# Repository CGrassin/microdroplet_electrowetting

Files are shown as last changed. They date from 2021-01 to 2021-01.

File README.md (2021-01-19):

# µDroplet - Microfluidics platform

Microfluidics is an area of research based on the manipulation of small fluid volumes on the order of microliters or nanoliters.

µDroplet is an open-source platform with an 8&times;8 array of electrodes driven by a high voltage to expermiment with various microfluidics techniques and materials.

See article here: https://charleslabs.fr/en/project-Microfluidics+Electrowetting+platform

## Content

This repository contains:
* The PCB (including BOM and gerber files),
* The Arduino firmware
* The Processing control software
* The STL/CAD files for the 3D-printable base and frame

## License

The content of this repository is under MIT license.

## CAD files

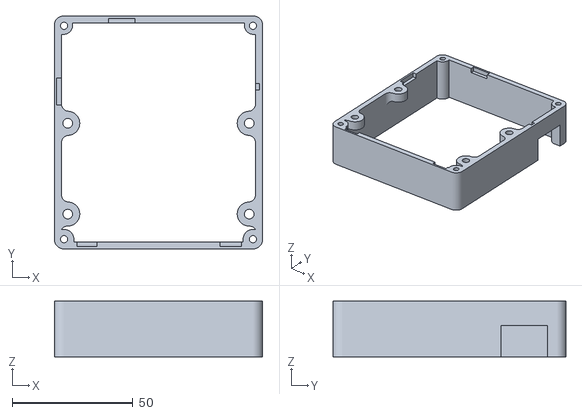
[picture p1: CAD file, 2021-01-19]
Microfluidics_CAD/microfluidics_base.STL
86.4 x 96.5 x 23.0

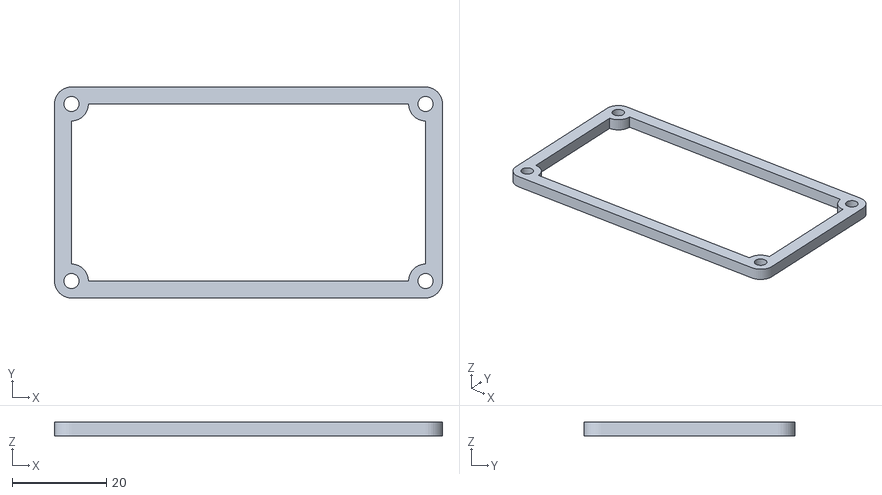
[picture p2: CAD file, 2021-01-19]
Microfluidics_CAD/microfluidics_lid.STL
82.4 x 44.8 x 3.00

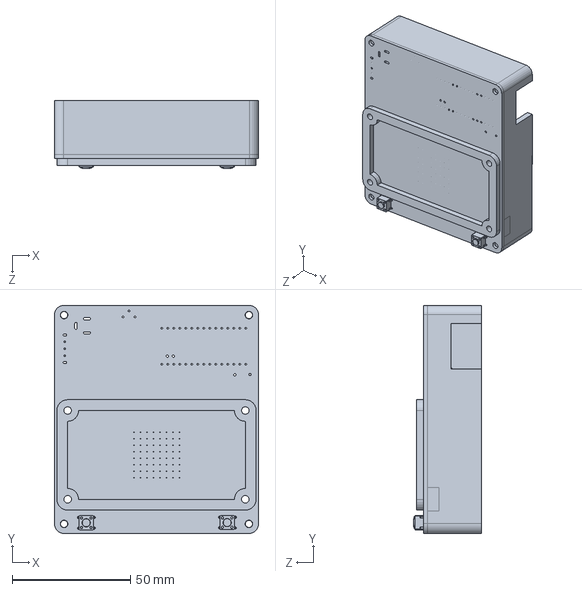
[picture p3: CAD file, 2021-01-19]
Microfluidics_CAD/MicroDroplet_PCB.SLDPRT
86.4 x 96.5 x 29.0 mm

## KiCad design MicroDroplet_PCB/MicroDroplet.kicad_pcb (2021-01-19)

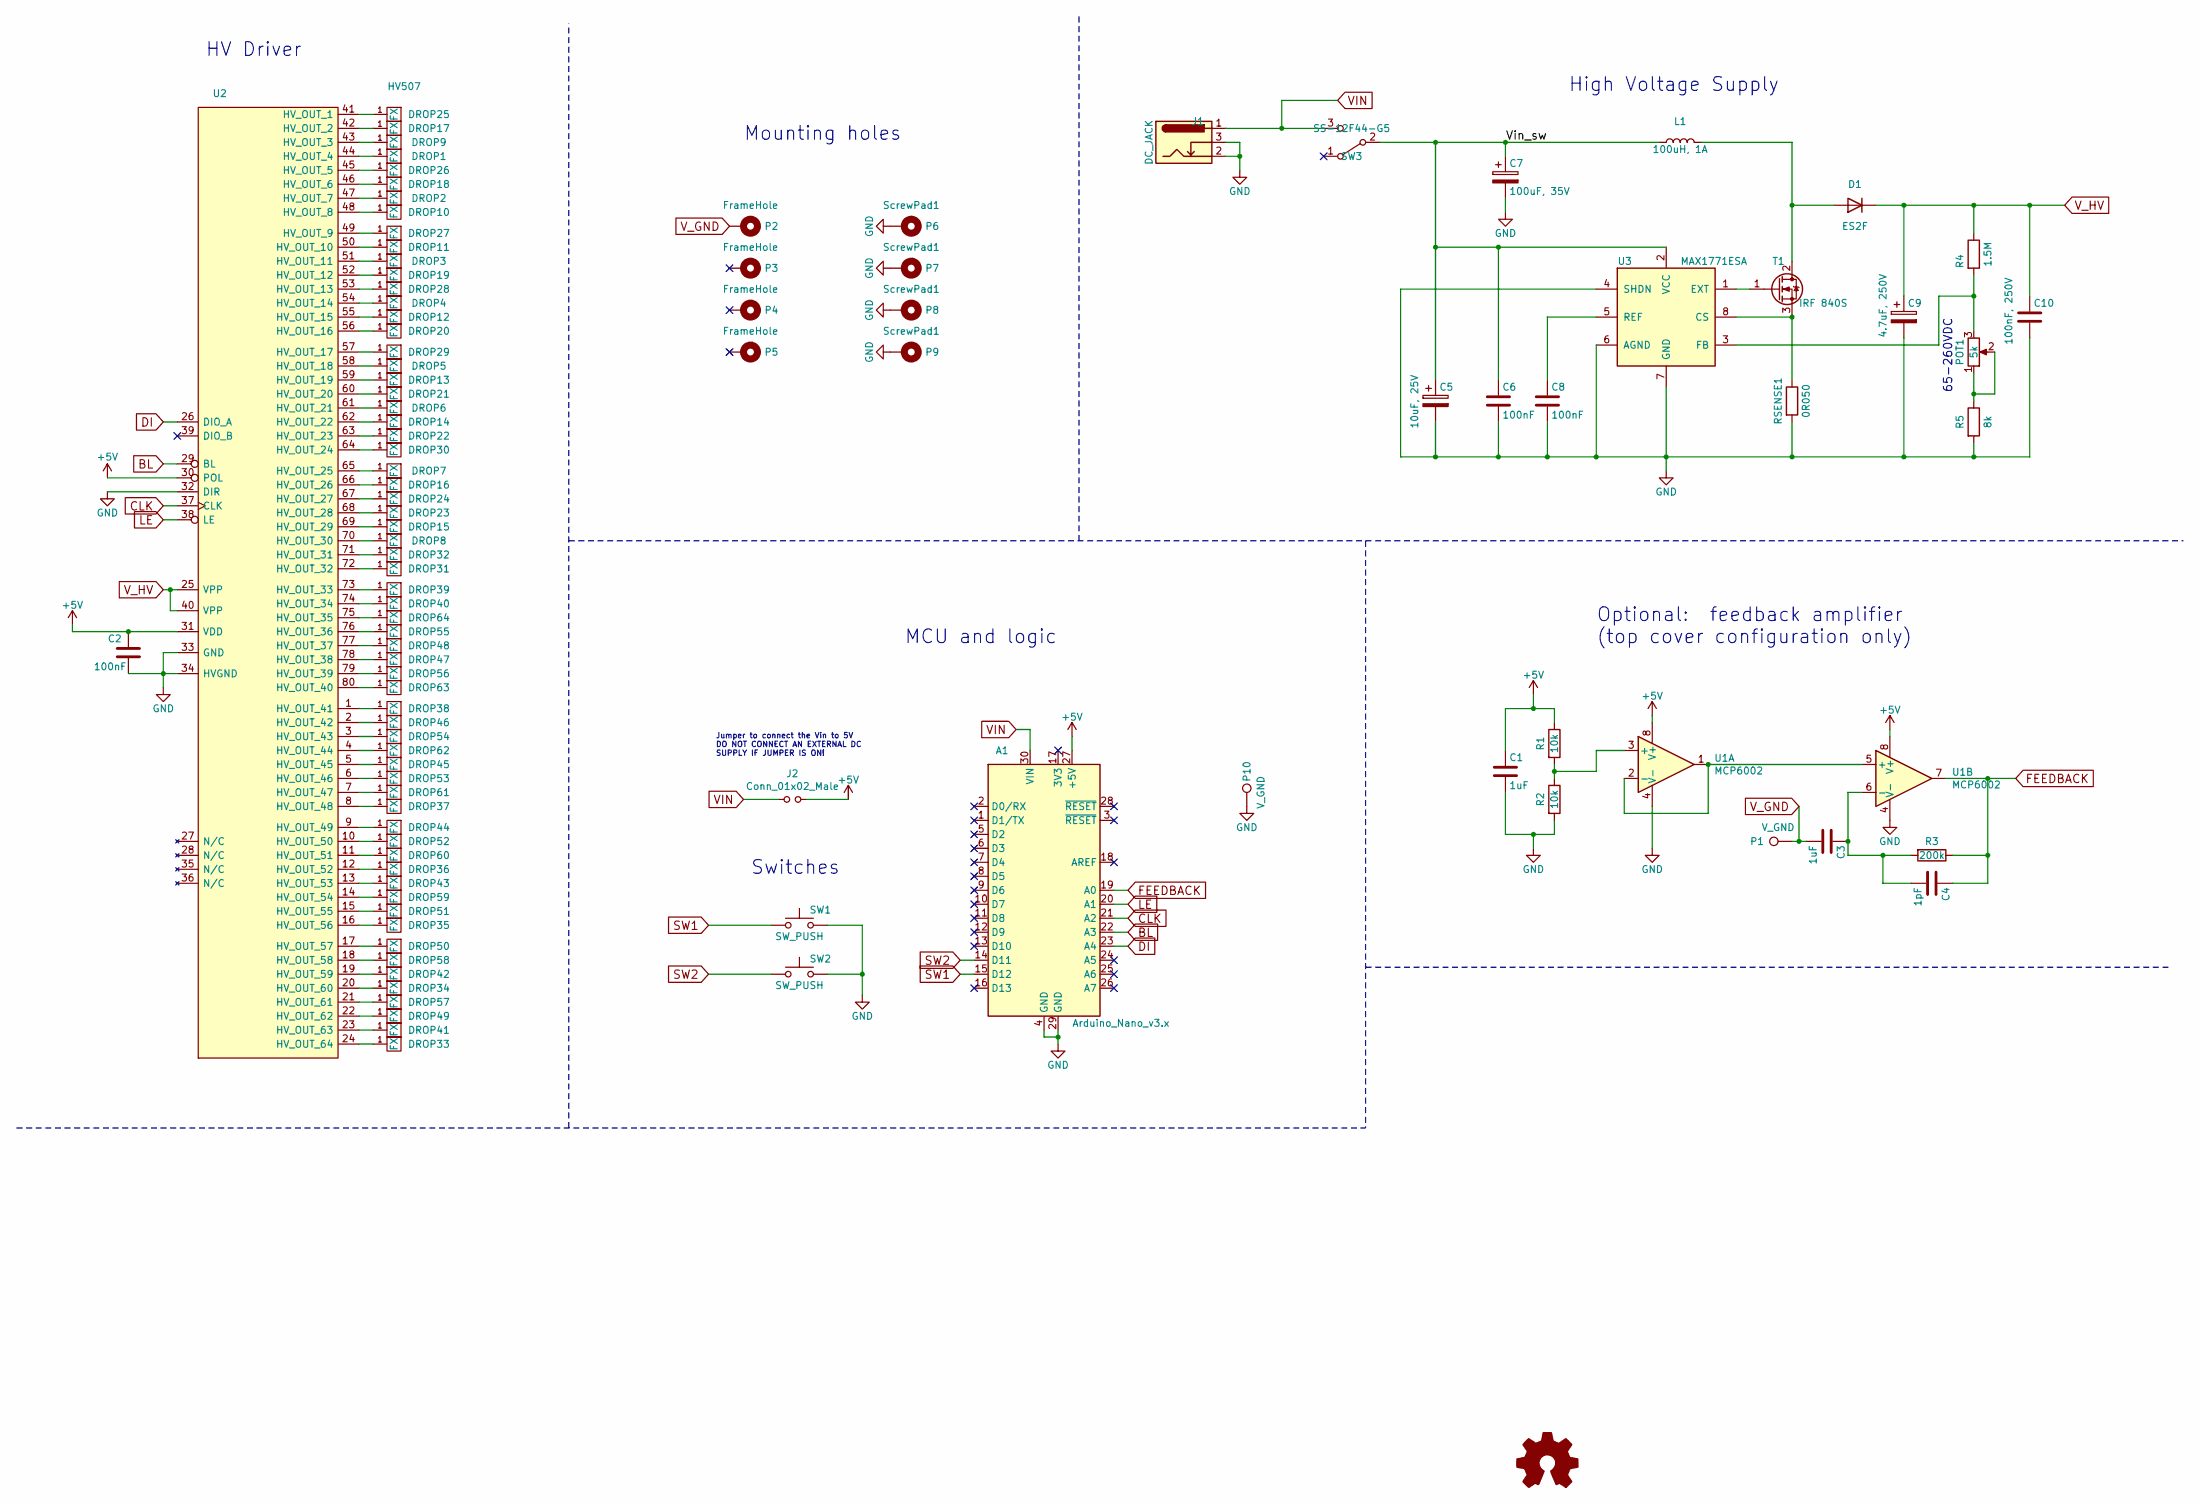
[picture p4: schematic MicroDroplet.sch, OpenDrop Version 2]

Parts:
A1: Arduino_Nano_v3.x; Arduino_Nano
C1, C3: 1uF; C_0805_2012Metric_Pad1.15x1.40mm_HandSolder; LCSC C28323
C2, C6, C8: 100nF; C_0805_2012Metric_Pad1.15x1.40mm_HandSolder; LCSC C476766
C4: 1pF; C_0805_2012Metric_Pad1.15x1.40mm_HandSolder; LCSC C1786
C5: 10uF, 25V; CP_Elec_5x5.4; LCSC C72487
C7: 100uF, 35V; CP_Elec_6.3x7.7; LCSC C99837
C9: 4.7uF, 250V; CP_Elec_10x10.5; LCSC C88703
C10: 100nF, 250V; C_1206_3216Metric_Pad1.42x1.75mm_HandSolder; LCSC C338139
D1: ES2F; D_SMB_Handsoldering; LCSC C145321
DROP1, DROP2, DROP3, DROP4, DROP5, DROP6, DROP7, DROP8, DROP9, DROP10, DROP11, DROP12, DROP13, DROP14, DROP15, DROP16, DROP17, DROP18, DROP19, DROP20, DROP21, DROP22, DROP23, DROP24, DROP25, DROP26, DROP27, DROP28, DROP29, DROP30, DROP31, DROP32, DROP33, DROP34, DROP35, DROP36, DROP37, DROP38, DROP39, DROP40, DROP41, DROP42, DROP43, DROP44, DROP45, DROP46, DROP47, DROP48, DROP49, DROP50, DROP51, DROP52, DROP53, DROP54, DROP55, DROP56, DROP57, DROP58, DROP59, DROP60, DROP61, DROP62, DROP63, DROP64: FX; DROP_2_75_4MIL_4_5
J1: DC_JACK; BarrelJack_Horizontal; LCSC C16214
J2: Conn_01x02_Male; PinHeader_1x02_P2.54mm_Vertical; LCSC C124375
L1: 100uH, 1A; L_Bourns_SRR1210A; LCSC C237992
LOGO1: Logo_Open_Hardware_Small; Charleslabs_Logo_10mm
P1, P10: V_GND; TestPoint_THTPad_D2.0mm_Drill1.0mm
P2: FrameHole; MountingHole_3.2mm_M3_Pad
P3, P4, P5: FrameHole; MountingHole_3.2mm_M3
P6, P7, P8, P9: ScrewPad1; MountingHole_3.2mm_M3_Pad
POT1: 5k; BOURNS-3362P_pot; LCSC C116296
R1, R2: 10k; R_0805_2012Metric_Pad1.15x1.40mm_HandSolder; LCSC C38522
R3: 200k; R_0805_2012Metric_Pad1.15x1.40mm_HandSolder; LCSC C104082
R4: 1.5M; R_1206_3216Metric_Pad1.42x1.75mm_HandSolder; LCSC C294796
R5: 8k; R_0805_2012Metric_Pad1.15x1.40mm_HandSolder; LCSC C465485
RSENSE1: 0R050; R_2512_6332Metric_Pad1.52x3.35mm_HandSolder; LCSC C160588
SW1, SW2: SW_PUSH; SW_PUSH_6mm; LCSC C393938
SW3: SS-12F44-G5; SPDT_12.1_5.6; LCSC C136718
T1: IRF 840S; TO-263-2; LCSC C134927
U1: MCP6002; SOIC-8_3.9x4.9mm_P1.27mm; LCSC C7377
U2: HV507; PQFP-80_14x20mm_P0.8mm
U3: MAX1771ESA; SOIC-8_3.9x4.9mm_P1.27mm

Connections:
+5V: A1.27 (+5V), C1.1, C2.1, J2.2, R1.1, U1.8 (V+), U2.30 (POL), U2.31 (VDD)
/Vin_sw: C5.1, C6.1, C7.1, L1.1, SW3.2 (B), U3.2 (VCC)
BL: A1.22 (A3), U2.29 (BL)
CLK: A1.21 (A2), U2.37 (CLK)
DI: A1.23 (A4), U2.26 (DIO_A)
FEEDBACK: A1.19 (A0), C4.1, R3.1, U1.7
GND: A1.4 (GND), A1.29 (GND), C1.2, C2.2, C5.2, C6.2, C7.2, C8.2, C9.2, C10.2, J1.2, J1.3, P6.1, P7.1, P8.1, P9.1, P10.1, R2.2, R5.2, RSENSE1.2, SW1.2, SW2.2, U1.4 (V-), U2.32 (DIR), U2.33 (GND), U2.34 (HVGND), U3.4 (SHDN), U3.6 (AGND), U3.7 (GND)
LE: A1.20 (A1), U2.38 (LE)
unnamed: C3.1, C4.2, R3.2, U1.6 (-)
unnamed: C8.1, U3.5 (REF)
unnamed: D1.2 (A), L1.2, T1.2 (D)
unnamed: DROP1.1, U2.44 (HV_OUT_4)
unnamed: DROP2.1, U2.47 (HV_OUT_7)
unnamed: DROP3.1, U2.51 (HV_OUT_11)
unnamed: DROP4.1, U2.54 (HV_OUT_14)
unnamed: DROP5.1, U2.58 (HV_OUT_18)
unnamed: DROP6.1, U2.61 (HV_OUT_21)
unnamed: DROP7.1, U2.65 (HV_OUT_25)
unnamed: DROP8.1, U2.70 (HV_OUT_30)
unnamed: DROP9.1, U2.43 (HV_OUT_3)
unnamed: DROP10.1, U2.48 (HV_OUT_8)
unnamed: DROP11.1, U2.50 (HV_OUT_10)
unnamed: DROP12.1, U2.55 (HV_OUT_15)
unnamed: DROP13.1, U2.59 (HV_OUT_19)
unnamed: DROP14.1, U2.62 (HV_OUT_22)
unnamed: DROP15.1, U2.69 (HV_OUT_29)
unnamed: DROP16.1, U2.66 (HV_OUT_26)
unnamed: DROP17.1, U2.42 (HV_OUT_2)
unnamed: DROP18.1, U2.46 (HV_OUT_6)
unnamed: DROP19.1, U2.52 (HV_OUT_12)
unnamed: DROP20.1, U2.56 (HV_OUT_16)
unnamed: DROP21.1, U2.60 (HV_OUT_20)
unnamed: DROP22.1, U2.63 (HV_OUT_23)
unnamed: DROP23.1, U2.68 (HV_OUT_28)
unnamed: DROP24.1, U2.67 (HV_OUT_27)
unnamed: DROP25.1, U2.41 (HV_OUT_1)
unnamed: DROP26.1, U2.45 (HV_OUT_5)
unnamed: DROP27.1, U2.49 (HV_OUT_9)
unnamed: DROP28.1, U2.53 (HV_OUT_13)
unnamed: DROP29.1, U2.57 (HV_OUT_17)
unnamed: DROP30.1, U2.64 (HV_OUT_24)
unnamed: DROP31.1, U2.72 (HV_OUT_32)
unnamed: DROP32.1, U2.71 (HV_OUT_31)
unnamed: DROP33.1, U2.24 (HV_OUT_64)
unnamed: DROP34.1, U2.20 (HV_OUT_60)
unnamed: DROP35.1, U2.16 (HV_OUT_56)
unnamed: DROP36.1, U2.12 (HV_OUT_52)
unnamed: DROP37.1, U2.8 (HV_OUT_48)
unnamed: DROP38.1, U2.1 (HV_OUT_41)
unnamed: DROP39.1, U2.73 (HV_OUT_33)
unnamed: DROP40.1, U2.74 (HV_OUT_34)
unnamed: DROP41.1, U2.23 (HV_OUT_63)
unnamed: DROP42.1, U2.19 (HV_OUT_59)
unnamed: DROP43.1, U2.13 (HV_OUT_53)
unnamed: DROP44.1, U2.9 (HV_OUT_49)
unnamed: DROP45.1, U2.5 (HV_OUT_45)
unnamed: DROP46.1, U2.2 (HV_OUT_42)
unnamed: DROP47.1, U2.78 (HV_OUT_38)
unnamed: DROP48.1, U2.77 (HV_OUT_37)
unnamed: DROP49.1, U2.22 (HV_OUT_62)
unnamed: DROP50.1, U2.17 (HV_OUT_57)
unnamed: DROP51.1, U2.15 (HV_OUT_55)
unnamed: DROP52.1, U2.10 (HV_OUT_50)
unnamed: DROP53.1, U2.6 (HV_OUT_46)
unnamed: DROP54.1, U2.3 (HV_OUT_43)
unnamed: DROP55.1, U2.76 (HV_OUT_36)
unnamed: DROP56.1, U2.79 (HV_OUT_39)
unnamed: DROP57.1, U2.21 (HV_OUT_61)
unnamed: DROP58.1, U2.18 (HV_OUT_58)
unnamed: DROP59.1, U2.14 (HV_OUT_54)
unnamed: DROP60.1, U2.11 (HV_OUT_51)
unnamed: DROP61.1, U2.7 (HV_OUT_47)
unnamed: DROP62.1, U2.4 (HV_OUT_44)
unnamed: DROP63.1, U2.80 (HV_OUT_40)
unnamed: DROP64.1, U2.75 (HV_OUT_35)
unnamed: POT1.1, POT1.2, R5.1
unnamed: POT1.3, R4.2, U3.3 (FB)
unnamed: R1.2, R2.1, U1.3 (+)
unnamed: RSENSE1.1, T1.3 (S), U3.8 (CS)
unnamed: T1.1 (G), U3.1 (EXT)
unnamed: U1.1, U1.2 (-), U1.5 (+)
SW1: A1.15 (D12), SW1.1
SW2: A1.14 (D11), SW2.1
VIN: A1.30 (VIN), J1.1, J2.1, SW3.3 (C)
V_GND: C3.2, P1.1, P2.1
V_HV: C9.1, C10.1, D1.1 (K), R4.1, U2.25 (VPP), U2.40 (VPP)

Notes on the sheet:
65-260VDC
High Voltage Supply
HV Driver
Switches
Jumper to connect the Vin to 5V DO NOT CONNECT AN EXTERNAL DC SUPPLY IF JUMPER IS ON!
Optional: feedback amplifier (top cover configuration only)
Mounting holes
MCU and logic

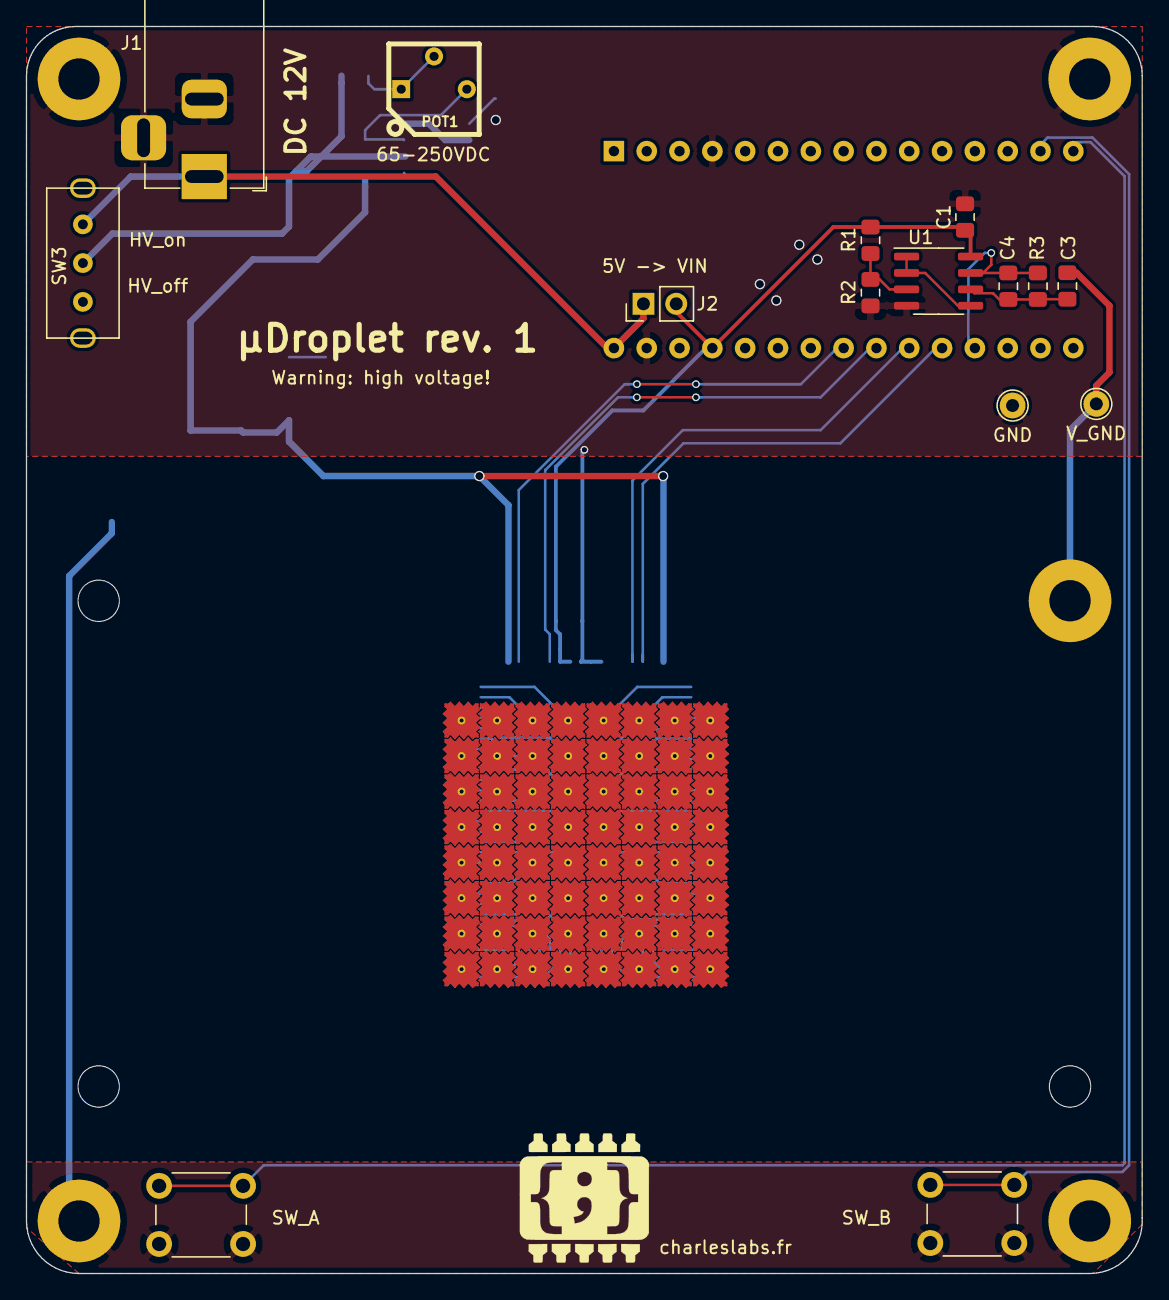
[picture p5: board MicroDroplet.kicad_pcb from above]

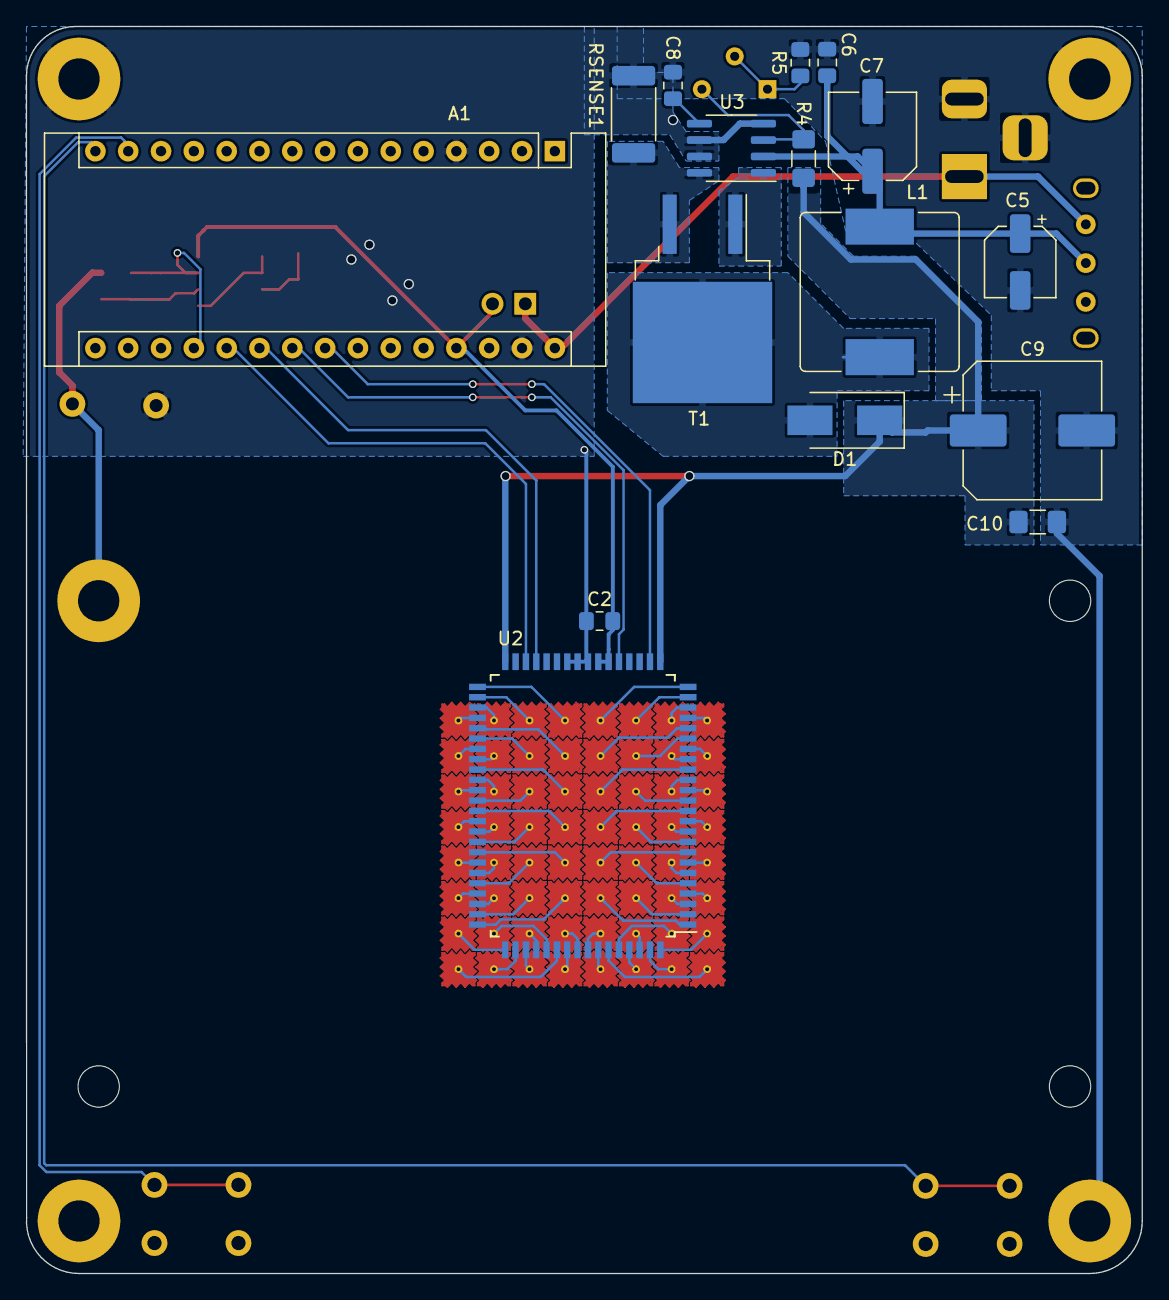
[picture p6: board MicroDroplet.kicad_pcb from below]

Board: 2 copper layers, 86.4 x 96.5 mm, 104 parts (16 on the bottom side), 86 nets.

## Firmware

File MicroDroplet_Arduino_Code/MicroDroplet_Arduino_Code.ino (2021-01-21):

/* MIT Open-Source LICENSE:
*
* Copyright 2018 Charles Grassin
* 
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
* THE SOFTWARE IS PROVIDED "AS IS", WITHOUT WARRANTY OF ANY KIND, 
* EXPRESS OR IMPLIED, INCLUDING BUT NOT LIMITED TO THE WARRANTIES OF 
* MERCHANTABILITY, FITNESS FOR A PARTICULAR PURPOSE AND NONINFRINGEMENT.
* IN NO EVENT SHALL THE AUTHORS OR COPYRIGHT HOLDERS BE LIABLE FOR ANY 
* CLAIM, DAMAGES OR OTHER LIABILITY, WHETHER IN AN ACTION OF CONTRACT,
* TORT OR OTHERWISE, ARISING FROM, OUT OF OR IN CONNECTION WITH THE 
* SOFTWARE OR THE USE OR OTHER DEALINGS IN THE SOFTWARE.
*/

// PINS
#define PIN_FEEDBACK (A0)
#define PIN_LE (A1)
#define PIN_CLK (A2)
#define PIN_BL (A3)
#define PIN_DI (A4)
#define PIN_SWA (12)
#define PIN_SWB (11)

// SETTINGS
#define ELECTRODE_ARRAY_WIDTH 8
#define ELECTRODE_ARRAY_HEIGHT 8
const byte HV507_LOOKUP_TABLE [] = {4,5,6,7,12,13,15,14,20,22,23,21,28,31,30,29,36,39,38,37,47,46,45,44,55,62,61,53,54,63,60,52,51,59,56,49,58,50,57,48,43,42,41,40,34,33,32,35,26,25,24,27,18,16,17,19,9,8,10,11,0,1,2,3};
#define BAUD_RATE 115200
#define SERIAL_BUFFER_LENGTH 10
#define TEST_PROG

// VARS
bool electrodes[ELECTRODE_ARRAY_WIDTH][ELECTRODE_ARRAY_HEIGHT];
char serialBuffer[SERIAL_BUFFER_LENGTH];
uint8_t currentIndex=0;

// Electrode array code
void clearElectrodes() {
  for (int x = 0; x <ELECTRODE_ARRAY_WIDTH ; x++) 
    for (int y = 0; y <ELECTRODE_ARRAY_HEIGHT ; y++) 
      setElectrode(x,y,false);
}

void setElectrodes() {
  for (int x = 0; x <ELECTRODE_ARRAY_WIDTH ; x++) 
    for (int y = 0; y <ELECTRODE_ARRAY_HEIGHT ; y++) 
    setElectrode(x,y,true);
}

void setElectrode(int x,int y,bool state) {
  if(state != electrodes[x][y]) {
    electrodes[x][y]=state;
    sendElectrode(x,y);
  }
}

void sendElectrode(int x,int y){
  Serial.print(x);
  Serial.print(",");
  Serial.print(y);
  Serial.print(",");
  Serial.print(electrodes[x][y]);
  Serial.print("\n");
}

// Refer to HV507 datasheet
void writeHV507() {
  digitalWrite(PIN_LE, LOW);
  digitalWrite(PIN_CLK, LOW);
   
  for (int i = 0; i <64 ; i++) {
    digitalWrite(PIN_DI,electrodes[HV507_LOOKUP_TABLE[i]%8][HV507_LOOKUP_TABLE[i]/8]);
    digitalWrite(PIN_CLK, HIGH);
    digitalWrite(PIN_CLK, LOW);
  }

  digitalWrite(PIN_LE, HIGH);
  digitalWrite(PIN_LE, LOW);
}

void setup() {
  Serial.begin(BAUD_RATE);
  
  pinMode(PIN_LE, OUTPUT);
  digitalWrite(PIN_LE,LOW);
  pinMode(PIN_CLK, OUTPUT);
  digitalWrite(PIN_CLK,LOW);
  pinMode(PIN_BL, OUTPUT);
  digitalWrite(PIN_BL,HIGH);
  pinMode(PIN_DI, OUTPUT);
  digitalWrite(PIN_DI,LOW);
  
  pinMode(PIN_SWA, INPUT_PULLUP);
  pinMode(PIN_SWB, INPUT_PULLUP);

  clearElectrodes();
  writeHV507();
  digitalWrite(PIN_BL,HIGH);

  for (int x = 0; x <ELECTRODE_ARRAY_WIDTH ; x++) 
    for (int y = 0; y <ELECTRODE_ARRAY_HEIGHT ; y++) 
      sendElectrode(x,y);
}

#ifdef TEST_PROG
  int step = 0;
  long unsigned int lastT = millis();
#endif

void loop() {
  if(serialReadCommand()){
    writeHV507();
  }

  // Test program
  #ifdef TEST_PROG
    if(millis()-lastT>500){
      lastT = millis();
      switch(step){
        case 0: setElectrode(4,3,false);
        setElectrode(4,4,true);
        break;
        case 1:setElectrode(4,4,false);
        setElectrode(4,5,true);
        break;
        case 2:setElectrode(4,5,false);
        setElectrode(5,5,true);
        break;
        case 3:setElectrode(5,5,false);
        setElectrode(5,4,true);
        break;
        case 4:setElectrode(5,4,false);
        setElectrode(5,3,true);
        break;
        case 5:setElectrode(5,3,false);
        setElectrode(4,3,true);
        break;
      }
      writeHV507();
      step ++;
      if(step > 5) step = 0;
    }
  #endif
}

uint8_t serialReadCommand(){
  uint8_t number_of_commands = 0;
  while (Serial.available() > 0) {
    char recieved = Serial.read();

    serialBuffer[currentIndex] = recieved;
    currentIndex ++;
    if (currentIndex >= SERIAL_BUFFER_LENGTH) {
      // Invalid command: command is too long
      currentIndex = 0;
    }

    if (recieved == '\n' || recieved == '\r') {
      // Close string
      serialBuffer[currentIndex-1] = '\0';
      
      // Clear buffer for next serial transaction
      currentIndex = 0; 

      // Split the string
      char* commaIndex = strchr(serialBuffer, ',');
      if (commaIndex==NULL) {
        // Invalid command: command is malformed
        continue;
      }
      commaIndex[0] = '\0';
      char* secondCommaIndex = strchr(commaIndex+1, ',');
      if (secondCommaIndex==NULL) {
        // Invalid command: command is malformed
        continue;
      }
      secondCommaIndex[0] = '\0';

      int x = atoi(serialBuffer);
      int y = atoi(commaIndex+1);
      if(x<0 || x>=ELECTRODE_ARRAY_WIDTH || y<0 || y>=ELECTRODE_ARRAY_HEIGHT){
        // Invalid command: out of bound
        continue;
      }
      
      setElectrode(x,y,strcmp(secondCommaIndex+1,"0")!=0);
      number_of_commands += 1;
    }
  }
  return number_of_commands;
}

/*void btnMatrixTest(){
  for (int y = 0; y <ELECTRODE_ARRAY_WIDTH ; y++) 
    for (int x = 0; x <ELECTRODE_ARRAY_HEIGHT ; x++){
      clearElectrodes();
      electrodes[x][y]=true;
      writeHV507();
      Serial.print(x);
      Serial.print("\t");
      Serial.println(y);
      delay(500);
      while(digitalRead(PIN_SWA)){}
    }
}*/
